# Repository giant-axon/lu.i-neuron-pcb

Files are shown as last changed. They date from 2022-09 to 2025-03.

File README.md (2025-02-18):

# Lu.i[¹](#footnote-1) – An educational neuron PCB

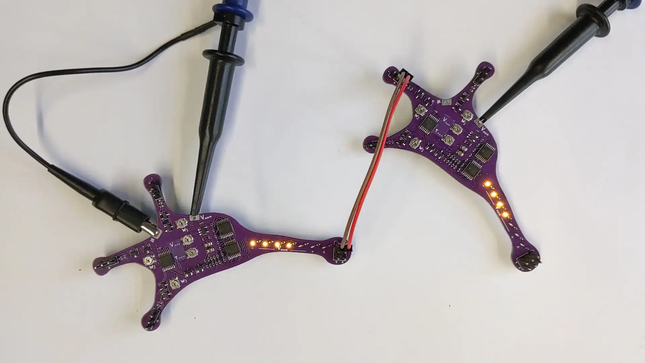
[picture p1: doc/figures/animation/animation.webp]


Lu.i is an electronic neuron circuit mimicking and illustrating the basic dynamics of real, biological neurons.
The printed circuit board (PCB) features a configurable, fully analog implementation of the leaky integrate-and-fire model and visualizes the internal state, the *membrane potential*, through a VU-meter-style chain of LEDs.
The neuron emits a short pulse whenever the membrane potential crosses a predefined threshold voltage.
Neurons communicate by exchanging these *spikes*.
Multiple boards can be connected via jumper wires to form networks.

<br/>

For a more detailed write-up you may refer to our manuscript:

**Lu. i – A low-cost electronic neuron for education and outreach**  
Yannik Stradmann, Julian Göltz, Mihai A. Petrovici, Johannes Schemmel, Sebastian Billaudelle (2025)  
Trends in Neuroscience and Education, Volume 38, 100248: [10.1016/j.tine.2025.100248](https://doi.org/10.1016/j.tine.2025.100248)

For inquiries feel free to contact us at [info@giantaxon.org](mailto:info@giantaxon.org).

## Features
- fully analog implementation of the leaky integrate-and-fire model
- configurable leak potential and membrane time constant
- three synapses with tunable weight and sign (excitatory or inhibitory) and shared synaptic time constant
- three output terminals to forward spikes to other neurons
- powered by a CR2032 coin battery
- Arduino-compatible (5V-tolerant spike IO)
- VU-meter-style visualization of the membrane potential and spike LED
- optimized for low-cost production (~ 3 € per neuron)

## Example Networks
Resembling the structure of the nervous system, multiple *Lu.i* boards can be connected to form complex neural networks.
They may be used for illustrative purposes, mimicking biological behavior, or even solving functional tasks.
The following hierarchical network, e.g., implements an *exclusive OR* (XOR).

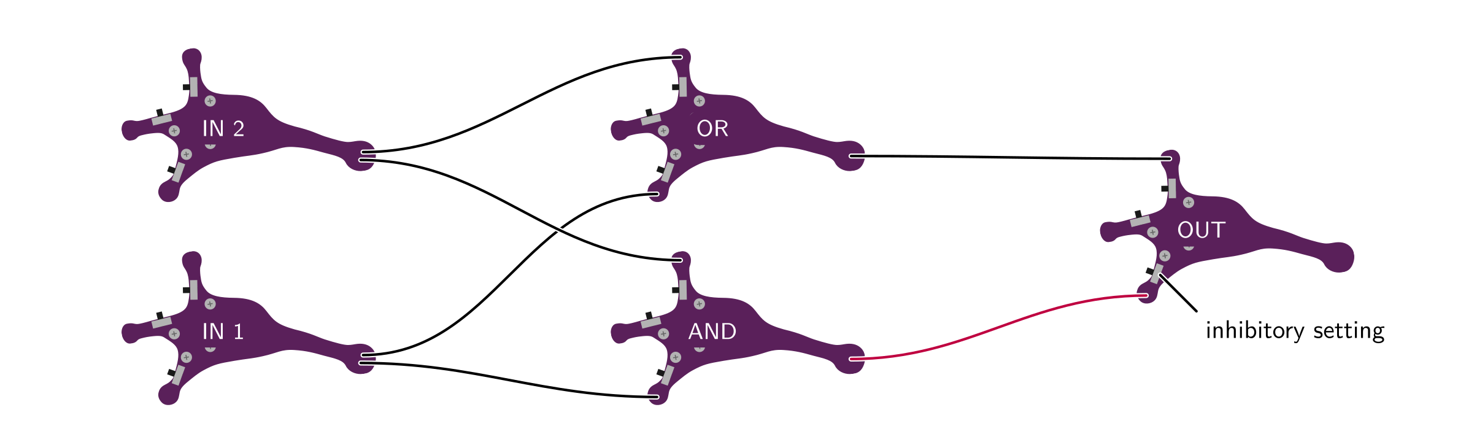
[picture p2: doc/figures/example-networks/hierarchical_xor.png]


For a more extensive list of example networks please refer to [Lu.i's documentation](doc/).

## Model
The neuron implemented on the PCBs is called Leaky Integrate-and-Fire (LIF) model.
For this model, the membrane voltage follows the dynamics described by the differential equation

$$
    \tau_\text{mem} \frac{\mathrm{d}V_\text{mem}}{\mathrm{d}t} = - \left(V_\text{mem} - V_\text{leak} \right) + I_{\text{syn}} / g_\text{leak}.
$$

In short, the neuron sums up its input $I_\text{syn}$ and decays back to the leak voltage $V_\text{leak}$.
The LIF model, including the spiking behavior when the threshold is reached, is implemented in electric circuits.

## Electronic Implementation
The following circuit diagram shows the different functional blocks of the analog implementation on *Lu.i*.
The full schematics are given as KiCAD design files.

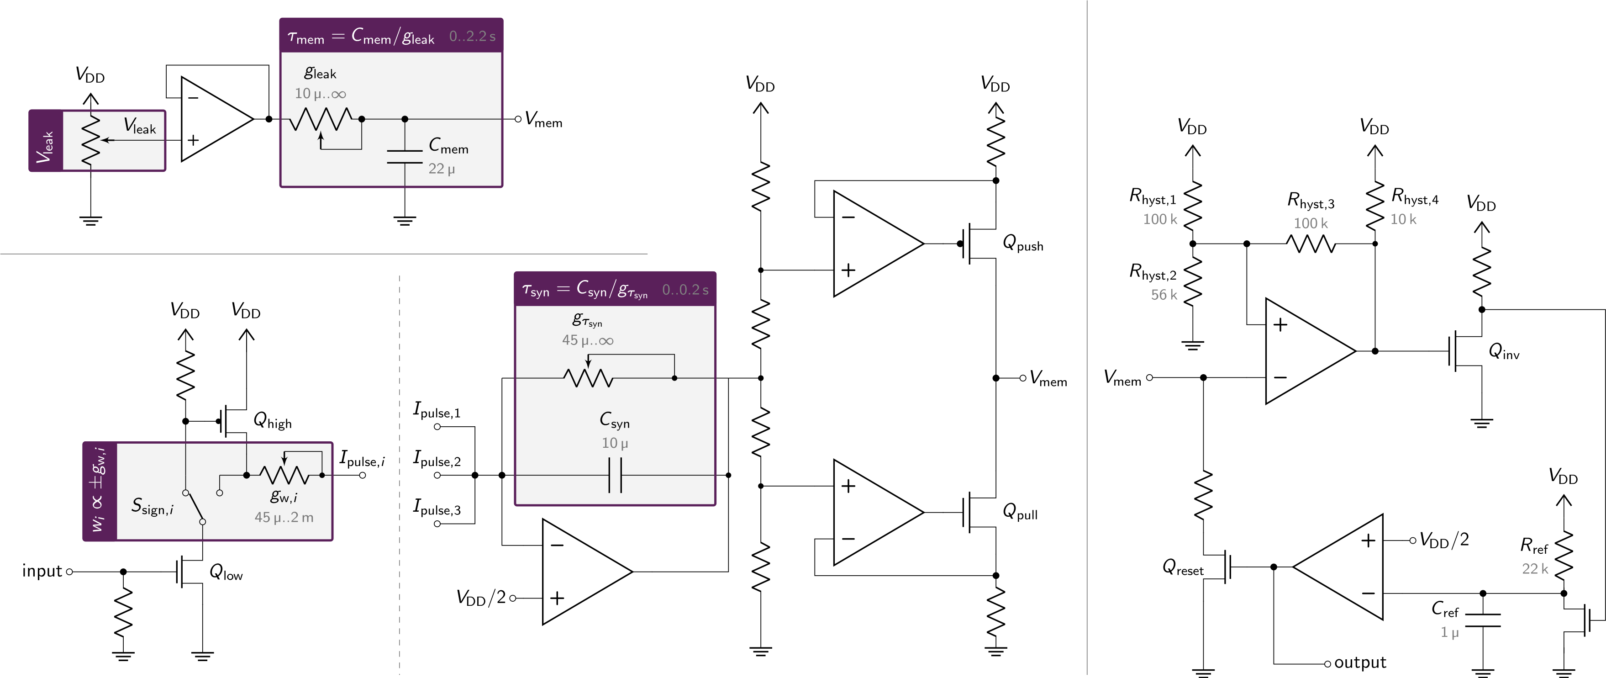
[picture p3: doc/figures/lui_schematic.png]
schematics


Besides the formation of synaptic connections between the individual neurons, inputs and outputs of each *Lu.i* can also be used to connect with a wide range of microcontrollers and sensors.
Example code can be found in the [documentation](doc/). 

## Manufacturing
The component choice in the *Lu.i* design is optimized for manufacturing at [JLCPCB](https://jlcpcb.com/).
With every [release](../../releases/), we include all the design files necessary for production.
Detailed instructions on the ordering process can be found in the [documentation](doc/).

---

<a name="footnote-1">¹</a> The name »Lu.i« (phonetic notation of »Louis«) is a tribute to Louis E. Lapicque, who first formulated the leaky integrate-and-fire equations modeling the dynamics of a neuron.

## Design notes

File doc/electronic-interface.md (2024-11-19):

# Lu.i's electronic interface

Each *Lu.i* neuron receives synaptic stimuli and sends out spike events in the form of rectangular pulses.

## Output signals
Each efferent spike creates a low-impedance voltage pulse at the axonal terminal of *Lu.i*.
These pulses are approximately 15 ms long and have a signal level of 2.5 V:

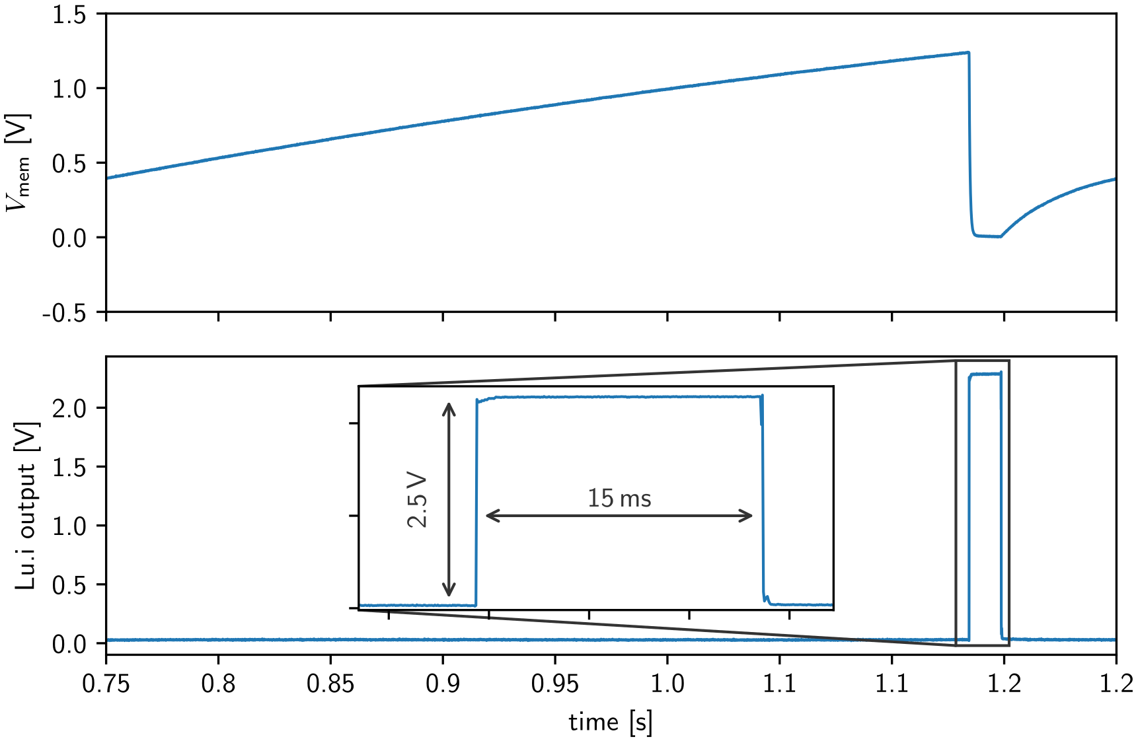
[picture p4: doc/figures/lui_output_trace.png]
Lui output trace


## Input signals
*Lu.i* decodes any voltage pulses above 1.8 V as an input event.
The amplitude does not scale the strength of the corresponding current and may therefore be of any value between 1.8 V and 20 V.
The pulse width, however, linearly scales the effective weight.

Users may create such input stimuli by external microcontrollers or sensors.
To ensure similar effective weights for such "virtual" inputs compared to other *Lu.i* neurons, the pulse length should be approximately 15 ms long.

## Example: Stimulus generation with Arduino
Using the common [Arduino](https://www.arduino.cc/) framework, we can define a simple function to create input stimuli.
For example, we can create a regular-spaced spike train:
```cpp
// Arduino pin connected to the Lu.i synapse
static constexpr uint8_t NEURON_PIN = 5;

void send_spike(uint8_t neuron_pin)
{
	digitalWrite(neuron_pin, true);
	delay(15);  // 15ms pulse length
	digitalWrite(neuron_pin, false);
}

void setup()
{
	pinMode(NEURON_PIN, OUTPUT);
}

void loop()
{
	send_spike(NEURON_PIN);
	delay(500); // 500ms inter spike interval
}
```

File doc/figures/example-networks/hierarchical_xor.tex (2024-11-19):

\documentclass[convert={density=300,outext=.png}]{standalone}
\input{preamble.tex}

\begin{document}

\tikzset{
  symbolGround/.pic = {
      \node(-m) [pic actions]{};
      \begin{scope}
          \draw[line cap=round] (0, 0) -- (0, 0.2);
          \draw[line cap=round] (-0.3, 0) -- (0.3, 0);
          \draw[line cap=round] (-0.2, -0.1) -- (0.2, -0.1);
          \draw[line cap=round] (-0.1, -0.2) -- (0.1, -0.2);
      \end{scope}
  },
  symbolMinus/.pic = {
      \node(-m) [pic actions]{};
      \begin{scope}
          \draw[line cap=round] (-0.2, 0) -- (0.2, 0);
      \end{scope}
  },
  symbolPlus/.pic = {
      \node(-m) [pic actions]{};
      \begin{scope}
          \draw[line cap=round] (0, -0.2) -- (0, 0.2);
          \draw[line cap=round] (-0.2, 0) -- (0.2, 0);
      \end{scope}
  }
}

\begin{tikzpicture}[
    scale=1.,
    >=latex,
    transform shape,
]
    \def\numNeuronsI{2}
    \def\numNeuronsH{2}
    \def\numNeuronsO{1}
    \def\scale{1.7}

    \def\posXI{-7}
    \def\posXH{-0.25}
    \def\posXO{6.5}

    \def\lengthSeparation{2.8}

    \def\angleNeuron{10}
    \def\angleOut{0}
    \def\angleIn{180}

    \foreach \i in {1,...,\numNeuronsI}
    {
        \pgfmathsetmacro\posYtmp{0 + \lengthSeparation * (\i - (\numNeuronsI + 1) / 2)}
        \pcbNeuron{neuron-I\i}{
            \posXI, \posYtmp
        }{\scale}{\angleNeuron}{}{}{tunab};
    }

    \foreach \i in {1,...,\numNeuronsH}
    {
        \pgfmathsetmacro\posYtmp{0 + \lengthSeparation * (\i - (\numNeuronsH + 1) / 2)}
        \pcbNeuron{neuron-H\i}{
            \posXH, \posYtmp
        }{\scale}{\angleNeuron}{}{}{tunab};
    }

    \foreach \i in {1,...,\numNeuronsO}
    {
        \pgfmathsetmacro\posYtmp{0 + \lengthSeparation * (\i - (\numNeuronsO + 1) / 2)}
        \pcbNeuron{neuron-O\i}{
            \posXO, \posYtmp
        }{\scale}{\angleNeuron}{}{}{tunab};
    }

    % %%%%%%%%%%%%% connections
    % % input hidden
    \draw[connection] (neuron-I1-Ac) to[out=\angleOut,in=\angleIn] (neuron-H1-Dc);
    \draw[connection] (neuron-I1-Aa) to[out=\angleOut,in=\angleIn] (neuron-H2-Dc);
    %
    \draw[connection] (neuron-I2-Ac) to[out=\angleOut,in=\angleIn] (neuron-H1-Da);
    \draw[connection] (neuron-I2-Aa) to[out=\angleOut,in=\angleIn] (neuron-H2-Da);

    % % hidden output
    \draw[connection, purple] (neuron-H1-Ab) to[out=\angleOut,in=\angleIn] (neuron-O1-Dc);
    %
    \draw[connection] (neuron-H2-Ab) to[out=\angleOut,in=\angleIn] (neuron-O1-Da);
    %

    % %%%%%%%%%%%%% labels
    \tikzstyle{specialNeuronlabel} = [neuronlabel, fill=pcbcolour, rounded corners=.15cm]
    \node[specialNeuronlabel] at (neuron-I1-l) {IN 1};
    \node[specialNeuronlabel] at (neuron-I2-l) {IN 2};
    \node[specialNeuronlabel] at (neuron-H1-l) {AND};
    \node[specialNeuronlabel] at (neuron-H2-l) {OR};
    \node[specialNeuronlabel] at (neuron-O1-l) {OUT};

    % redraw inhibitory switch
    \node[anchor=north west] (tmp) at ([xshift=0.5cm, yshift=-0.5cm]neuron-O1-tun-WSc) {inhibitory setting};
    \draw[connection] (neuron-O1-tun-WSc) -- (tmp.north west);
	
    \begin{scope}[on background layer]
    	\node[minimum width=20cm, fit=(current bounding box.north west) (current bounding box.south east), inner sep=2pt, fill=white] {};
    \end{scope}
\end{tikzpicture}
\end{document}

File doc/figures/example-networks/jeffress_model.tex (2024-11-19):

\documentclass[convert={density=300,outext=.png}]{standalone}
\nonstopmode
\input{preamble.tex}

\begin{document}

\begin{tikzpicture}[
    scale=1.,
    >=latex,
    transform shape,
]
    \def\numNeurons{4}
    \def\scale{1.3}
    \def\halfAngleConnection{10}
    \def\angleNeuron{10}
    \def\posXoffsetTop{-10.4}
    \def\posXoffsetMiddle{-8.0}
    \def\posXoffsetBottom{-3.4}
    \def\lengthSeparation{3.5}
    \def\angleOut{-20}
    \def\angleIn{180}

    % % draw ellipse on which the neurons lie
    % \draw (0,0) ellipse (\axlengthA cm and \axlengthB cm );

    % neurons
    \foreach \i in {2,...,\numNeurons}
    {
        % delay Top
        \pcbNeuron{nDelayTop-\i}{
            \posXoffsetTop + \i * \lengthSeparation, 3
        }{\scale}{\angleNeuron}{}{}{};
        % delay bottm
        \pgfmathsetmacro{\xPosition}{\posXoffsetBottom + (\numNeurons - \i) * \lengthSeparation}
        \pcbNeuron{nDelayBottom-\i}{
            \xPosition, -3
        }{\scale}{\angleNeuron + 180}{}{}{};

        % \node[neuronlabel, font=\sffamily\tiny, ] at (nDelayTop-\i) {nDelayTop-\i};
        % \node[neuronlabel, font=\sffamily\tiny, ] at (nDelayBottom-\i) {nDelayBottom-\i};
    }

    % coincidence
    \foreach \i in {1,...,\numNeurons}
    {
        \pcbNeuron{nCoinci-\i}{
            \posXoffsetMiddle + \i * \lengthSeparation, 0
        }{\scale}{\angleNeuron}{}{}{};

        % \node[neuronlabel, font=\sffamily\tiny, ] at (nCoinci-\i) {nCoinci-\i};
    }

    % connections Delay
    \foreach \i in {2,...,\numNeurons}
    {
        \pgfmathtruncatemacro\nexts{ifthenelse(\i==\numNeurons, 1, round(\i+1))}
        \ifthenelse{\equal{\i}{\numNeurons}}{}{
            \draw[connection] (nDelayTop-\i-Ab) to[out=\angleOut,in=\angleIn] (nDelayTop-\nexts-Db);
            \draw[connection] (nDelayBottom-\i-Ab) to[out=\angleOut+180,in=\angleIn+180] (nDelayBottom-\nexts-Db);
        }
    }

    % connections Top to coincidence
    \foreach \i in {1,...,\numNeurons}
    {
        \ifthenelse{\equal{\i}{1}}{}{
            \draw[connection] (nDelayTop-\i-Ac) to[out=\angleOut,in=\angleIn-70] (nCoinci-\i-Da);
        }
        \ifthenelse{\equal{\i}{\numNeurons}}{}{
            \pgfmathtruncatemacro\nMinusI{round(\numNeurons-\i+1)}
            \draw[connection] (nDelayBottom-\nMinusI-Ac) to[out=\angleOut+180,in=\angleIn+40] (nCoinci-\i-Dc);
        }
    }

    % external stimulus

    \coordinate (ears) at (0, -6);
    \coordinate (cableIntermediateBottom) at ([yshift=0cm, xshift=2cm]nDelayBottom-2-Db);
    \coordinate (cableIntermediateTop) at ([yshift=-2cm, xshift=-2cm]nDelayTop-2-Db);

    \draw[connection] ([xshift=1mm]ears) to[out=90, in=-90] (cableIntermediateBottom) to[out=90,in=\angleIn+180] (nDelayBottom-2-Db);
    \draw[connection] (cableIntermediateBottom) to[out=90,in=\angleIn+40] (nCoinci-4-Dc);

    \draw[connection] ([xshift=-1mm]ears) to[out=90, in=-45] ([yshift=-0.5cm, xshift=-2cm]nDelayBottom-\numNeurons) to[out=-45+180, in=-90] (cableIntermediateTop) to[out=90,in=\angleIn] (nDelayTop-2-Db);
    \draw[connection] (cableIntermediateTop) to[out=90,in=\angleIn-70] (nCoinci-1-Da);

    \begin{scope}[on background layer]
    	\node[minimum width=20cm, fit=(current bounding box.north west) (current bounding box.south east), inner sep=2pt, fill=white] {};
    \end{scope}

    \begin{scope}[on background layer]
    	\node[minimum width=20cm, fit=(current bounding box.north west) (current bounding box.south east), inner sep=2pt, fill=white] {};
    \end{scope}
\end{tikzpicture}
\end{document}

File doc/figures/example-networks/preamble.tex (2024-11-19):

\usepackage{tikz}
\usepackage{svg}

\usetikzlibrary{shapes.geometric}
\usetikzlibrary{arrows.meta}
\usetikzlibrary{positioning}
\usetikzlibrary{calc}
\usetikzlibrary{backgrounds}
\usetikzlibrary{fit}
\usetikzlibrary{fadings}
\usetikzlibrary{decorations}
\usepgflibrary{decorations.pathmorphing}
\usepgflibrary{decorations.markings}

\renewcommand{\familydefault}{\sfdefault}
\usepackage{sansmathfonts}

\usepackage{rotating}

\definecolor{pcbcolour}{RGB}{90, 32, 90}
\definecolor{VULEDon}{RGB}{255, 128, 0}
\definecolor{VULEDoff}{RGB}{229, 207, 184}
% \colorlet{VULEDoff}{VULEDon!0.9!white}%

% for organising the multi-panel figures
% \tikzset{panel/.style={inner sep=0pt, }};
% \tikzset{panellabel/.style={anchor=north west, inner sep=0pt, font={\bfseries\sffamily}}};
\tikzstyle{panel} = [
    inner sep=0pt,
]
\tikzstyle{panellabel} = [
    anchor=north west,
    inner sep=0pt,
    font={\bfseries\sffamily},
]
\definecolor{cExcitatory}{RGB}{255, 77, 77}
\definecolor{cInhibitory}{RGB}{0, 51, 204}
\definecolor{cBGInhibitory}{RGB}{153, 194, 255}

\tikzstyle{connection} = [
    line width=1.0pt,
    preaction={draw,white,line width=2pt, line cap=round},
    line cap=round,
    ]
\tikzstyle{connectionSmall} = [
    line width=0.5pt,
    preaction={draw,white,line width=1pt, line cap=round},
    line cap=round,
    ]

\tikzstyle{inhibitory} = [
    line width=1.0pt,
    color=cInhibitory,
    preaction={draw,white,line width=2pt, line cap=round, -{Bar[scale=0.4,sep=-1.0pt]}},
    -{Bar[scale=0.4,sep=-0.5pt]},
    ]
\tikzstyle{excitatory} = [
    line width=1.0pt,
    color=cExcitatory,
    preaction={draw,white,line width=2pt, line cap=round, -{Latex[round, scale=0.6,sep=-1.8pt]}},
    -{Latex[round, scale=0.6,sep=-0.4pt]},
    ]

\tikzstyle{neuronlabel} = [
    white,
    font=\sffamily\small,
    ]

\newcommand{\ledVU}[7]{
    % macro for sketch used in overviews
    % arg1: name of nodes
    % arg2: position of node 
    % arg3: argScale
    % arg4: how many membrane lights are on
    % arg5: is spikeLED on
    % arg6: fill bkgnd
    % arg7: draw
    % %%%%%%%%%%%%% draw stuff
    \ifthenelse{ \equal{#3}{} }{
        \def\argScale{1}
    }{
        \def\argScale{#3}
    }
    \pgfmathsetmacro\halfWidth{0.4mm * \argScale}
    \pgfmathsetmacro\segmentHalfHeight{0.4mm * \argScale}
    \pgfmathsetmacro\segmentSeparation{0.3mm * \argScale}
    \def\spikeSeparation{2.5}  % in fractions of segment separation
    \def\LEDseparation{0.2mm * \argScale}

    \pgfmathsetmacro\totalHeight{\segmentHalfHeight*2*7 + \segmentSeparation * (5 + \spikeSeparation) + 2 * \LEDseparation}
    \coordinate (#1) at (#2);
    \coordinate (#1-bottom) at ([yshift=-\totalHeight]#1);
    \coordinate (#1-bottomL) at ([xshift=-\halfWidth - \LEDseparation]#1-bottom);
    \coordinate (#1-bottomR) at ([xshift=\halfWidth + \LEDseparation]#1-bottom);
    \coordinate (#1-L) at ([xshift=-\halfWidth - \LEDseparation]#1);
    \coordinate (#1-R) at ([xshift=\halfWidth + \LEDseparation]#1);
    
    \def\VULEDon{VULEDon}
    \def\VULEDoff{VULEDoff}

    \ifthenelse{ \equal{#6}{} }{ \def\optBknd{none} }{ \def\optBknd{pcbcolour} }
    \ifthenelse{ \equal{#7}{} }{ \def\optDraw{none} }{ \def\optDraw{pcbcolour} }
    \draw [
        shape=rectangle, anchor=center,
        fill=\optBknd,
        draw=\optDraw,
        line width=0.4pt * \argScale,
        % decorate, decoration={
        %     zigzag,segment length=0.5mm * \argScale, amplitude=.04mm * \argScale
        % },
        % minimum width=2mm * \argScale, minimum height=8mm * \argScale,
    ] (#1-L) rectangle (#1-bottomR);

    % define coords
    \foreach \i in {0,...,5}
    {
        \pgfmathsetmacro\height{\segmentHalfHeight*(2*\i+1)+ \segmentSeparation*\i + \LEDseparation};
        \coordinate (#1-LED\i) at ([yshift=\height]#1-bottom);
    };
    \pgfmathsetmacro\height{\segmentHalfHeight*(2*6+1) + \segmentSeparation * (5 + \spikeSeparation) + \LEDseparation};
    \coordinate (#1-LEDspike) at ([yshift=\height]#1-bottom);

    % draw stuff
    \foreach \i in {0,...,5}
    {
        \pgfmathsetmacro\iPlusOne{\i + 1};
        \ifthenelse{\i < #4}{\def\state{VULEDon}}{\def\state{VULEDoff}}
        \draw [
            fill=\state,
            draw=none,
        ] ([xshift=-\halfWidth, yshift=-\segmentHalfHeight]#1-LED\i) rectangle ([xshift=\halfWidth, yshift=\segmentHalfHeight]#1-LED\i) ;
        \ifthenelse{\i < #4}{
            \foreach \a in {0, 45, 90, 135, ..., 360}
            {
            \draw[
                rotate=\a,
                shorten <=1pt,
                draw=VULEDon,
            ] (#1-LED\i) -- ++(0.08*\argScale, 0);
            }
        }{}
    };
    \ifthenelse{ \equal{#5}{} }{\def\state{VULEDoff}}{\def\state{VULEDon}}
    \draw [
        fill=\state,
        draw=none,
    ] ([xshift=-\halfWidth, yshift=-\segmentHalfHeight]#1-LEDspike) rectangle ([xshift=\halfWidth, yshift=\segmentHalfHeight]#1-LEDspike) ;
    \ifthenelse{ \equal{#5}{} }{}{
            \foreach \a in {0, 45, 90, 135, ..., 360}
            {
            \draw[
                rotate=\a,
                shorten <=1pt,
                draw=VULEDon,
            ] (#1-LEDspike) -- ++(0.08*\argScale, 0);
            }
    }
}

\newcommand{\pcbNeuron}[7]{
    % macro for sketch used in overviews
    % arg1: name of nodes
    % arg2: point of node 
    % arg3: argScale
    % arg4: rotation
    % arg5: if nonempty, use only border shape of PCB
    % arg6: if nonempty, draw LEDs (arg6 are on, if >6 spiking)
    % arg7: if nonempty, draw tunabels
    % %%%%%%%%%%%%% draw stuff

    \ifthenelse{ \equal{#3}{} }{
        \def\argScale{1}
    }{
        \def\argScale{#3}
    }
    \ifthenelse{ \equal{#4}{} }{
        \def\rot{0}
    }{
        \def\rot{#4}
    }

    \coordinate (#1) at (#2);

    % label coord
    \coordinate (#1-l) at ([yshift=0.4mm * \argScale, xshift=0.6mm * \argScale] #2);

    \node[anchor=center,
          xshift=0.25cm * \argScale,yshift=0.1cm * \argScale, 
          rotate around={\rot:(#1)},
          ] (whitehead) at (#1)
    {
        % \scaledWidth
        \scalebox{\argScale}{
            \ifthenelse{ \equal{#5}{} }{
                \includesvg[width=2cm]{neuron_filled.svg}
            }{
                \includesvg[width=2cm]{neuron_border.svg}
            }
        }
    };

    % %%%%%%%%%%%%%%%%%%% dendrites
    \pgfmathsetmacro{\lengthDaX}{-0.09cm * \argScale}
    \pgfmathsetmacro{\lengthDaY}{0.64cm * \argScale}
    \coordinate[rotate around={\rot:(#1)}] (#1-Da) at ([xshift=\lengthDaX, yshift=\lengthDaY] #1);

    \pgfmathsetmacro{\lengthDbX}{-0.685cm * \argScale}
    \pgfmathsetmacro{\lengthDbY}{0.138cm * \argScale}
    \coordinate[rotate around={\rot:(#1)}]  (#1-Db) at ([xshift=\lengthDbX, yshift=\lengthDbY] #1);

    \pgfmathsetmacro{\lengthDcX}{-0.47cm * \argScale}
    \pgfmathsetmacro{\lengthDcY}{-0.42cm * \argScale}
    \coordinate[rotate around={\rot:(#1)}]  (#1-Dc) at ([xshift=\lengthDcX, yshift=\lengthDcY] #1);

    % %%%%%%%%%%%%%%%%%%% axons
    \pgfmathsetmacro{\lengthAaX}{1.150cm * \argScale}
    \pgfmathsetmacro{\lengthAaY}{-0.360cm * \argScale}
    \coordinate[rotate around={\rot:(#1)}]  (#1-Aa) at ([xshift=\lengthAaX, yshift=\lengthAaY] #1);

    \pgfmathsetmacro{\lengthAbX}{1.135cm * \argScale}
    \pgfmathsetmacro{\lengthAbY}{-0.390cm * \argScale}
    \coordinate[rotate around={\rot:(#1)}]  (#1-Ab) at ([xshift=\lengthAbX, yshift=\lengthAbY] #1);

    \pgfmathsetmacro{\lengthAcX}{1.120cm * \argScale}
    \pgfmathsetmacro{\lengthAcY}{-0.420cm * \argScale}
    \coordinate[rotate around={\rot:(#1)}]  (#1-Ac) at ([xshift=\lengthAcX, yshift=\lengthAcY] #1);

    % %%%%%%%%%%%%%%%%%%% LEDs
    \pgfmathsetmacro{\lengthLEDX}{0.770cm * \argScale}
    \pgfmathsetmacro{\lengthLEDY}{-0.205cm * \argScale}
    \pgfmathsetmacro{\newscaling}{\argScale * 0.8}  % isn't tex beautiful..
    \coordinate[rotate around={\rot:(#1)}] (#1-LEDs) at ([xshift=\lengthLEDX, yshift=\lengthLEDY] #1);
    \ifthenelse{ \equal{#6}{} }{}{
        \ifthenelse{ #6 > 6}{
            \node[rotate=244+\rot] (tmp) at (#1-LEDs) {
                \begin{tikzpicture}[
                ]
                \ledVU{luiLED}{0, 0}{\newscaling}{0}{yes}{}{} ;
                \end{tikzpicture}
            };
        }{
            \node[rotate=244+\rot] (tmp) at (#1-LEDs) {
                \begin{tikzpicture}[
                ]
                \ledVU{luiLED}{0, 0}{\newscaling}{#6}{}{}{} ;
                \end{tikzpicture}
            };
        };
    }

    % %%%%%%%%%%%%%%%%%%% tunables
    \pgfmathsetmacro{\lengthTunPotiRad}{1.29 * \argScale}
    \pgfmathsetmacro{\lengthTunPotiScrew}{0.59 * \argScale}

    \pgfmathsetmacro{\lengthTunVleakX}{-0.059cm * \argScale}
    \pgfmathsetmacro{\lengthTunVleakY}{0.135cm * \argScale}
    \pgfmathsetmacro{\lengthTunTaumX}{-0.059cm * \argScale}
    \pgfmathsetmacro{\lengthTunTaumY}{0.029cm * \argScale}
    \pgfmathsetmacro{\lengthTunTausX}{-0.059cm * \argScale}
    \pgfmathsetmacro{\lengthTunTausY}{-0.076cm * \argScale}
    \coordinate[rotate around={\rot:(#1)}] (#1-tun-v_leak) at ([xshift=\lengthTunVleakX, yshift=\lengthTunVleakY] #1);
    \coordinate[rotate around={\rot:(#1)}] (#1-tun-taum) at ([xshift=\lengthTunTaumX, yshift=\lengthTunTaumY] #1);
    \coordinate[rotate around={\rot:(#1)}] (#1-tun-taus) at ([xshift=\lengthTunTausX, yshift=\lengthTunTausY] #1);

    % weight potis
    \pgfmathsetmacro{\lengthTunWaX}{0.0cm * \argScale}
    \pgfmathsetmacro{\lengthTunWaY}{0.264cm * \argScale}
    \pgfmathsetmacro{\lengthTunWbX}{-0.329cm * \argScale}
    \pgfmathsetmacro{\lengthTunWbY}{0.076cm * \argScale}
    \pgfmathsetmacro{\lengthTunWcX}{-0.265cm * \argScale}
    \pgfmathsetmacro{\lengthTunWcY}{-0.129cm * \argScale}
    \coordinate[rotate around={\rot:(#1)}] (#1-tun-Wa) at ([xshift=\lengthTunWaX, yshift=\lengthTunWaY] #1);
    \coordinate[rotate around={\rot:(#1)}] (#1-tun-Wb) at ([xshift=\lengthTunWbX, yshift=\lengthTunWbY] #1);
    \coordinate[rotate around={\rot:(#1)}] (#1-tun-Wc) at ([xshift=\lengthTunWcX, yshift=\lengthTunWcY] #1);

    % drawing
    \ifthenelse{ \equal{#7}{} }{}{
        \foreach \iOtherIterator in {v_leak, taum, taus, Wa, Wb, Wc}
        {
            \fill[black!30!white] (#1-tun-\iOtherIterator) circle (\lengthTunPotiRad pt) coordinate (tmp);
            \draw[black!60!white, rotate around={\rot:(tmp)}] (tmp) ++ (-\lengthTunPotiScrew pt, 0) -- ++(2 * \lengthTunPotiScrew pt, 0);
            \draw[black!60!white, rotate around={\rot:(tmp)}] (tmp) ++ (0, -\lengthTunPotiScrew pt) -- ++(0, 2 * \lengthTunPotiScrew pt);
        };
    }

    % weight switches
    \pgfmathsetmacro{\lengthTunWSaX}{-0.082cm * \argScale}
    \pgfmathsetmacro{\lengthTunWSaY}{0.394cm * \argScale}
    \pgfmathsetmacro{\lengthTunWSbX}{-0.412cm * \argScale}
    \pgfmathsetmacro{\lengthTunWSbY}{0.153cm * \argScale}
    \pgfmathsetmacro{\lengthTunWScX}{-0.329cm * \argScale}
    \pgfmathsetmacro{\lengthTunWScY}{-0.276cm * \argScale}
    \coordinate[rotate around={\rot:(#1)}] (#1-tun-WSa) at ([xshift=\lengthTunWSaX, yshift=\lengthTunWSaY] #1);
    \coordinate[rotate around={\rot:(#1)}] (#1-tun-WSb) at ([xshift=\lengthTunWSbX, yshift=\lengthTunWSbY] #1);
    \coordinate[rotate around={\rot:(#1)}] (#1-tun-WSc) at ([xshift=\lengthTunWScX, yshift=\lengthTunWScY] #1);

    % drawing
    \ifthenelse{ \equal{#7}{} }{}{
        \foreach \iOtherIterator / \angleUnrotated in {WSa/81, WSb/4, WSc/60}
        {
            \pgfmathsetmacro{\angleRotated}{\angleUnrotated + \rot}
            \fill[black!90!white, rotate around={\angleRotated:(#1-tun-\iOtherIterator)}] (#1-tun-\iOtherIterator) ++(-0.024*\argScale, 0.0) rectangle ++(0.047*\argScale, 0.118*\argScale);
            \fill[black!30!white, rotate around={\angleRotated:(#1-tun-\iOtherIterator)}] (#1-tun-\iOtherIterator) ++(-0.079*\argScale, 0.0) rectangle ++(0.159*\argScale, 0.059*\argScale);
        };
    }
}

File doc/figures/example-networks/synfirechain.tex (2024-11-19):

\documentclass[convert={density=300,outext=.png}]{standalone}
\input{preamble.tex}

\begin{document}

\begin{tikzpicture}[
    scale=1.,
    >=latex,
    transform shape,
]
    \def\numNeurons{5}
    \def\scale{1.3}
    \def\halfAngleConnection{10}
    \def\angleNeuron{10}
    \def\posXoffset{-10.4}
    \def\lengthSeparation{3.5}
    \def\angleOut{-20}
    \def\angleIn{180}

    % % draw ellipse on which the neurons lie
    % \draw (0,0) ellipse (\axlengthA cm and \axlengthB cm );

    % neurons
    \foreach \i in {1,...,\numNeurons}
    {
        \pcbNeuron{neuron-\i}{
            \posXoffset + \i * \lengthSeparation, 0
        }{\scale}{\angleNeuron}{}{}{};
    }

    % connections
    \foreach \i in {1,...,\numNeurons}
    {
        \pgfmathtruncatemacro\nexts{ifthenelse(\i==\numNeurons, 1, round(\i+1))}
        \ifthenelse{\equal{\i}{\numNeurons}}{}{
            \draw[connection] (neuron-\i-Ab) to[out=\angleOut,in=\angleIn] (neuron-\nexts-Db);
        }
    }

    \begin{scope}[on background layer]
    	\node[minimum width=20cm, fit=(current bounding box.north west) (current bounding box.south east), inner sep=2pt, fill=white] {};
    \end{scope}

    \begin{scope}[on background layer]
    	\node[minimum width=20cm, fit=(current bounding box.north west) (current bounding box.south east), inner sep=2pt, fill=white] {};
    \end{scope}
\end{tikzpicture}
\end{document}

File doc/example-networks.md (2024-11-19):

# Example networks

## Synfire chain
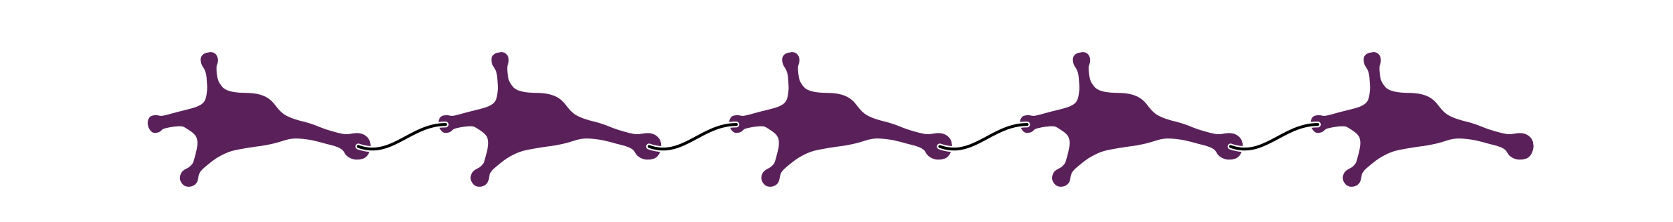
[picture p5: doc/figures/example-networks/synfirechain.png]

The name synfire chain is an abbreviation for synchronous firing chain and describes a circular feed-forward chain, in which activity travels from layer to layer.
When suitably configured, a spike in one of our neurons will elicit a consecutive spike in the next neuron in the chain.

This can also be put in a circular shape where the activity travels indefinitely.
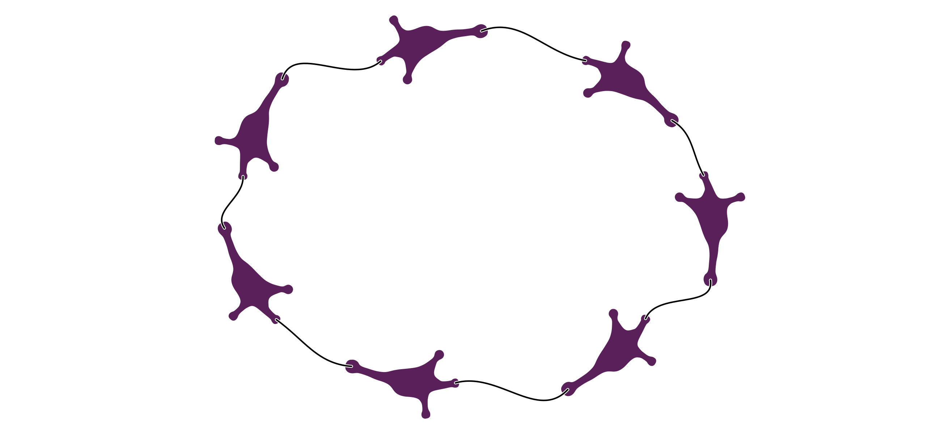
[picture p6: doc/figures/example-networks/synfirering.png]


Two synfirechains together with a set of coincidence-detecting neurons, can be used to realise a simplified version of the [Jeffress model](http://www.scholarpedia.org/article/Jeffress_model):
given two stimuli, their time difference determines which of the coincidence neurons is activated.
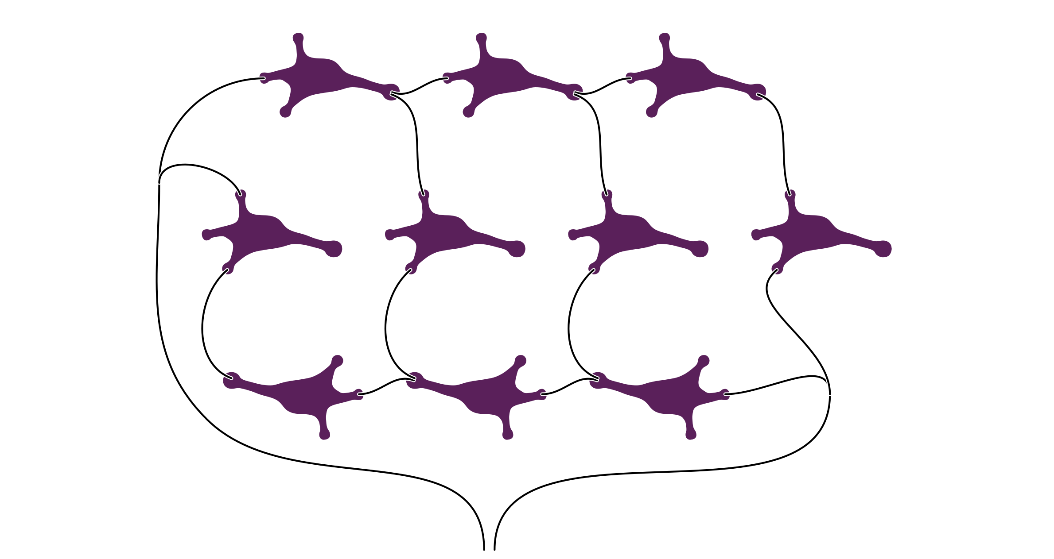
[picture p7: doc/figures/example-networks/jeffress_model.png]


## General hierarchical network
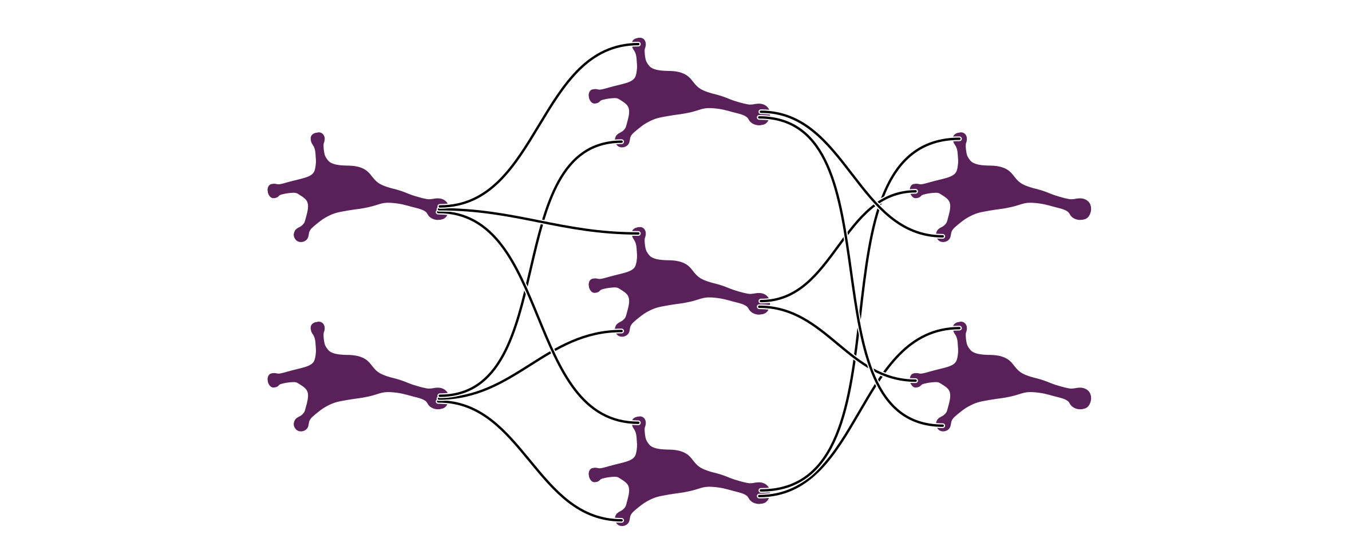
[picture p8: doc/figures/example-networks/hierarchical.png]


## Solving the XOR problem rate based


## Ring attractor
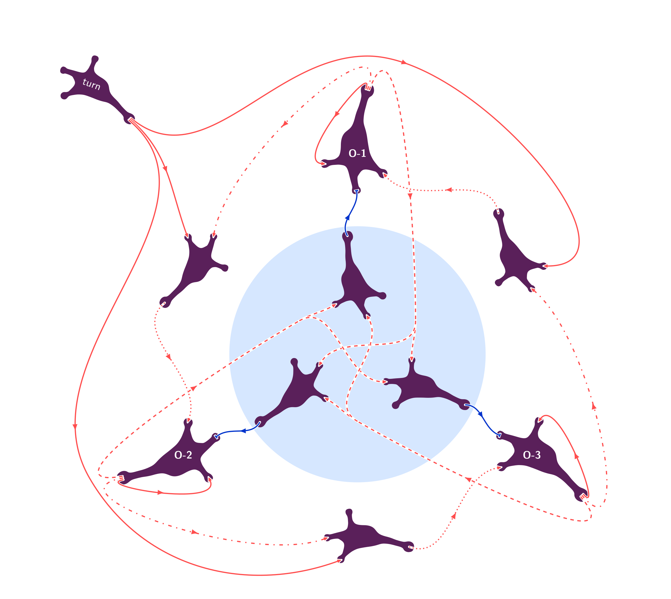
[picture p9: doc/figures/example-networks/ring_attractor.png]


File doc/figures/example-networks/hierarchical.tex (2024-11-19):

\documentclass[convert={density=300,outext=.png}]{standalone}
\input{preamble.tex}

\begin{document}
\begin{tikzpicture}[
    scale=1.,
    >=latex,
    transform shape,
]
    \def\numNeuronsI{2}
    \def\numNeuronsH{3}
    \def\numNeuronsO{2}
    \def\scale{1.3}

    \def\posXI{-5}
    \def\posXH{-0.25}
    \def\posXO{4.5}

    \def\lengthSeparation{2.8}

    \def\angleNeuron{10}
    \def\angleOut{0}
    \def\angleIn{180}

    \foreach \i in {1,...,\numNeuronsI}
    {
        \pgfmathsetmacro\posYtmp{0 + \lengthSeparation * (\i - (\numNeuronsI + 1) / 2)}
        \pcbNeuron{neuron-I\i}{
            \posXI, \posYtmp
        }{\scale}{\angleNeuron}{}{}{};
    }

    \foreach \i in {1,...,\numNeuronsH}
    {
        \pgfmathsetmacro\posYtmp{0 + \lengthSeparation * (\i - (\numNeuronsH + 1) / 2)}
        \pcbNeuron{neuron-H\i}{
            \posXH, \posYtmp
        }{\scale}{\angleNeuron}{}{}{};

    }

    \foreach \i in {1,...,\numNeuronsO}
    {
        \pgfmathsetmacro\posYtmp{0 + \lengthSeparation * (\i - (\numNeuronsO + 1) / 2)}
        \pcbNeuron{neuron-O\i}{
            \posXO, \posYtmp
        }{\scale}{\angleNeuron}{}{}{};
    }

    % %%%%%%%%%%%%% connections
    % % input hidden
    \draw[connection] (neuron-I1-Ac) to[out=\angleOut,in=\angleIn] (neuron-H1-Dc);
    \draw[connection] (neuron-I1-Ab) to[out=\angleOut,in=\angleIn] (neuron-H2-Dc);
    \draw[connection] (neuron-I1-Aa) to[out=\angleOut,in=\angleIn] (neuron-H3-Dc);
    %
    \draw[connection] (neuron-I2-Ac) to[out=\angleOut,in=\angleIn] (neuron-H1-Da);
    \draw[connection] (neuron-I2-Ab) to[out=\angleOut,in=\angleIn] (neuron-H2-Da);
    \draw[connection] (neuron-I2-Aa) to[out=\angleOut,in=\angleIn] (neuron-H3-Da);

    % % hidden output
    \draw[connection] (neuron-H1-Ac) to[out=\angleOut,in=\angleIn] (neuron-O1-Da);
    \draw[connection] (neuron-H1-Aa) to[out=\angleOut,in=\angleIn] (neuron-O2-Da);
    %
    \draw[connection] (neuron-H2-Ac) to[out=\angleOut,in=\angleIn] (neuron-O1-Db);
    \draw[connection] (neuron-H2-Aa) to[out=\angleOut,in=\angleIn] (neuron-O2-Db);
    %
    \draw[connection] (neuron-H3-Ac) to[out=\angleOut,in=\angleIn] (neuron-O1-Dc);
    \draw[connection] (neuron-H3-Aa) to[out=\angleOut,in=\angleIn] (neuron-O2-Dc);
	
    \begin{scope}[on background layer]
    	\node[minimum width=20cm, fit=(current bounding box.north west) (current bounding box.south east), inner sep=2pt, fill=white] {};
    \end{scope}
\end{tikzpicture}
\end{document}

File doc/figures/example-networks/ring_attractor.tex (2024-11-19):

\documentclass[convert={density=300,outext=.png}]{standalone}
\nonstopmode
\input{preamble.tex}

\begin{document}

\begin{tikzpicture}[
    scale=1.,
    >=latex,
    transform shape,
    decoration={
        markings,
        mark=at position 0.5 with {\arrow{>}}},
]
    \def\numNeurons{3}
    \def\scale{1.3}
    \def\nOrientationScale{1.6}
    \def\nOrientationRadius{6}
    \def\nOrientationAngle{10}
    \def\nInhibRadius{2.0}
    \def\nInhibAngle{30}
    \def\nSwitchRadius{5.5}
    \def\nSwitchAngle{160}
    \def\nTurnAngle{-20}

    \tikzstyle{signalSelfExc} = [excitatory, solid]
    \tikzstyle{signalToSwitch} = [excitatory, loosely dashdotted]
    \tikzstyle{signalSwitch} = [excitatory, dotted]
    \tikzstyle{signalToInhib} = [excitatory, dashed]
    \tikzstyle{signalTurn} = [excitatory, solid]

    \draw[draw=none, fill=cBGInhibitory!40] (0,0) circle (\nInhibRadius + \scale * 1.4);

    % neurons
    \foreach \i in {1,...,\numNeurons}
    {
        \pgfmathsetmacro\angle{360/\numNeurons * (\i-1) + 90}

        \pcbNeuron{nOrientation-\i}{
            {\angle}:\nOrientationRadius
        }{\nOrientationScale}{\angle + \nOrientationAngle}{}{}{};
        \node[neuronlabel] at (nOrientation-\i) {\textbf{O-\i}};

        \pcbNeuron{nInhib-\i}{
            {\angle}:\nInhibRadius
        }{\scale}{\angle + \nInhibAngle}{}{}{};

        \pcbNeuron{nSwitch-\i}{
            {\angle + 180 / \numNeurons}:\nSwitchRadius
        }{\scale}{\angle + \nSwitchAngle}{}{}{};

    }
    \pcbNeuron{nTurn}{-8, 8}{\scale}{\nTurnAngle}{}{}{};
    \node[neuronlabel, rotate=\nTurnAngle] at (nTurn-l) {turn};

    % connections
    \foreach \i in {1,...,\numNeurons}
    {
        \pgfmathsetmacro\angle{360/\numNeurons * (\i-1) + 90}

        \pgfmathtruncatemacro\iPlusOne{round(Mod(\i + 1 - 1, 3) + 1)}
        \pgfmathtruncatemacro\iPlusTwo{round(Mod(\i + 2 - 1, 3) + 1)}
        \pgfmathsetmacro\anglePlusOne{360/\numNeurons * (\iPlusOne-1) + 90}
        \pgfmathsetmacro\anglePlusTwo{360/\numNeurons * (\iPlusTwo-1) + 90}

        % self connections
        \draw[signalSelfExc, postaction={decorate}] (nOrientation-\i-Aa) to[out=\angle + \nOrientationAngle-30,in=\angle + \nOrientationAngle+180-105] (nOrientation-\i-Da);

        % inhibitory
        \draw[inhibitory, postaction={decorate}] (nInhib-\i-Ab) to[out=\angle + \nInhibAngle,in=\angle + \nOrientationAngle+180] (nOrientation-\i-Db);

        % to inhibitory
        \draw[signalToInhib, postaction={decorate}] (nOrientation-\i-Ac)
            to[out=\angle + \nOrientationAngle-30,
                in=\angle-0] (\angle - 180 / \numNeurons:\nInhibRadius)
            to[out=\angle-0+180,
               in=\anglePlusTwo + \nOrientationAngle+180-70] (nInhib-\iPlusTwo-Da);
        \draw[signalToInhib] (\angle - 180 / \numNeurons:\nInhibRadius)
            to[out=\angle-0+180,
               in=\anglePlusOne + \nOrientationAngle+180-70+ 90] (nInhib-\iPlusOne-Db);

           % switch
        \draw[signalSwitch, postaction={decorate}] (nSwitch-\i-Ab) to[out=\angle + \nOrientationAngle+\nSwitchAngle+180/\numNeurons - 100,in=\angle + \nOrientationAngle-30] (nOrientation-\iPlusOne-Dc);

        % to switch
        \draw[signalToSwitch, postaction={decorate}] (nOrientation-\i-Ab) to[out=\angle + \nOrientationAngle-30,in=\angle + \nOrientationAngle+\nSwitchAngle+180/\numNeurons + 120] (nSwitch-\i-Db);

    }

    % from turn
    \draw[signalTurn, postaction={decorate}] (nTurn-Aa) to[out=\nTurnAngle - 20,in=180] ([yshift=1cm]nOrientation-1-Ab) to[out=0,in=0] (nSwitch-3-Dc);
    \draw[signalTurn, postaction={decorate}] (nTurn-Ab) to[out=\nTurnAngle - 20,in=110]  (nSwitch-1-Dc);
    \def\tmp{120}
    \draw[signalTurn, postaction={decorate}] (nTurn-Ac) to[out=\nTurnAngle - 20,in=\tmp] ([xshift=-1cm]nOrientation-2-Ab) to[out=\tmp+180,in=200] (nSwitch-2-Dc);

    \begin{scope}[on background layer]
    	\node[minimum width=20cm, fit=(current bounding box.north west) (current bounding box.south east), inner sep=2pt,
            fill=white,
            ] {};
    \end{scope}
\end{tikzpicture}
\end{document}

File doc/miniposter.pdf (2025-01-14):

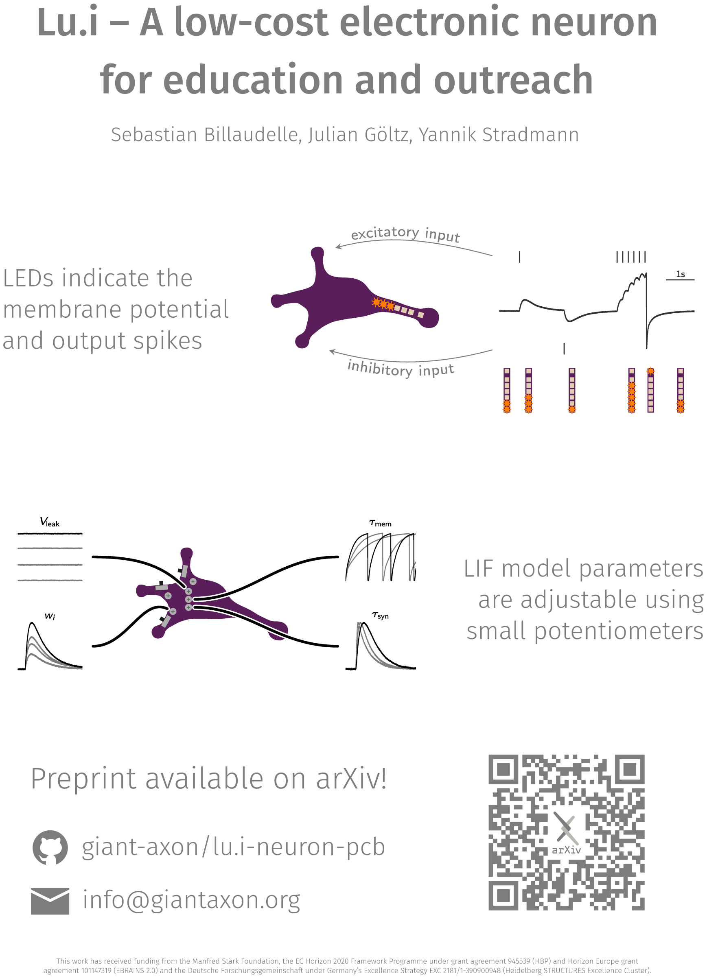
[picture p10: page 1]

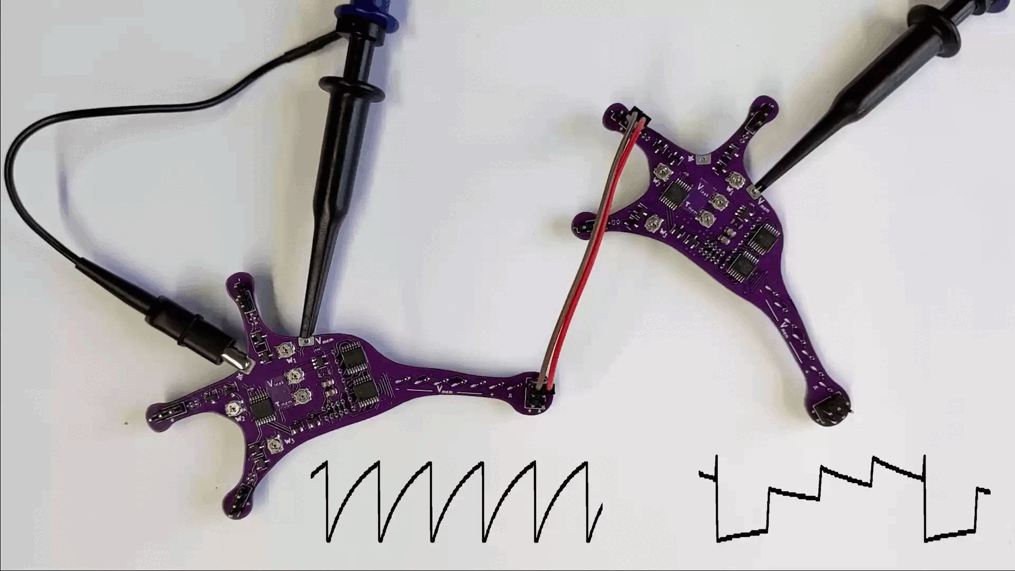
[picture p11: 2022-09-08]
doc/animation.gif

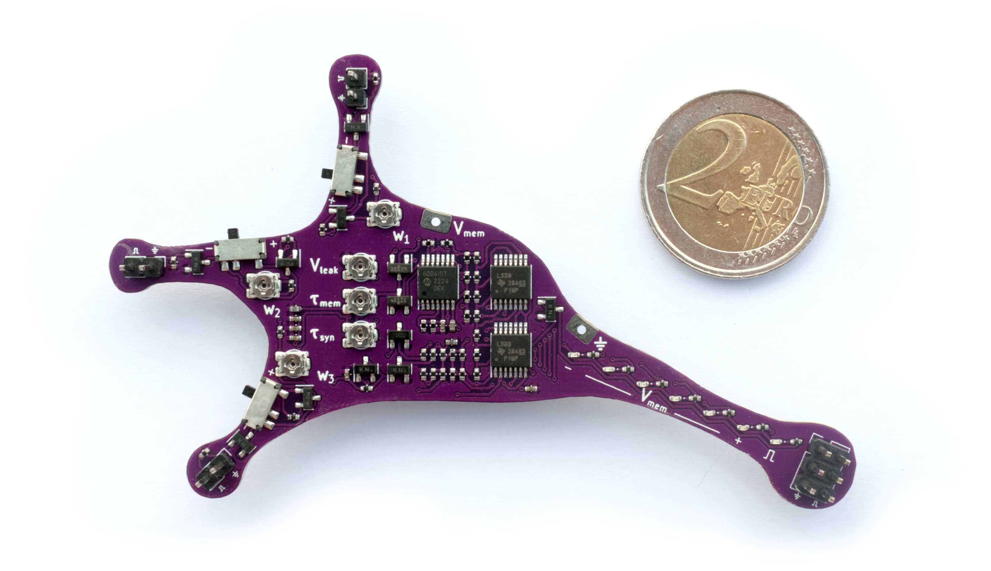
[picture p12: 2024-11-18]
doc/figures/photograph-coin.jpg

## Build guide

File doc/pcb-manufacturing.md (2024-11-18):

# Manufacturing of Lu.i boards
With every [release](../../../releases), we provide the necessary production files for orders at [JLCPCB](https://jlcpcb.com/).
We have used this manufacturer for over 1000 boards in multiple batches for the fabrication of the actual PCB as well as its assembly (PCBA).

> [!CAUTION]
> Although we never had issues during production and publish the production files to the best of our knowledge, we cannot take any liability for failed/disfunctional production runs.
Use this manual at your own risk.

## File structure
In our releases, you will find a file called `jlcpcb.zip`, which contains the following files:
```
jlcpcb.zip
├── …
├── production_files
│   ├── BOM-neuron.csv
│   ├── CPL-neuron.csv
│   └── GERBER-neuron.zip
└── …
```

* **GERBER-neuron.zip** contains the PCB production data in Gerber format, i.e., the layout of connections on the board, drilling information etc.
* **BOM-neuron.csv** contains the *bill of materials*, i.e., a list of all components on the board 
* **CPL-neuron.csv** contains the *component placement* information, i.e., where the components from the BOM should be placed during assembly

## Ordering process
Once you have created an account at JLCPCB and logged in, you can

### 1. Construct the PCB
- Upload the `GERBER-neuron.zip` and wait for processing
- The web interface wil automatically determine the number of layers (2), PCB size etc.
- Specify your *Lu.i* version at will, most importantly: PCB quantity.
  We've found that purple works great as PCB color.
  The design has no special requirements on copper weight, via structure etc. – the defaults should be good enough
- We like to remove the order number to clean up the silk screen
- We usually ask for a confirmation of the production file

### 2. Configure PCBA
- Enable the PCBA option (let JLCPCB assemble all components for you)
- Since *Lu.i* has components on both sides, a full production run requires "Standard" type and double-sided assembly.
- Just to be sure, we usually ask for a confirmation of the parts placement

> [!TIP]
> The bottom side only contains the battery holder and power switch.
Experts may select "top only" assembly, order remaining components independently and solder themselves.

### 3. Process BOM and CPL file
- In the next step, JLCPCB will ask you for the BOM and CPL files
- After processing, you may need to select alternative parts in case of shortfall (depends on your order quantity).
  For this step, a background in electronics can be handy.
  Alternatively, you may try to wait until missing components are re-stocked.
  If in doubt, ask your local expert :)
- Check the 3D model for obvious misplacement of any component

### 4. Place the order
> [!NOTE]
> *Lu.i* is published under the very permissive [CERN-OHL-S](../LICENSE) license.
If you want to fabricate your own version, please make sure to check that potential modifications comply.

- To add the design to your cart, you will need to specify a product category.
  We usually use `Education/Others` and mention the `TARIC ID 902300` ("Instruments, apparatus and models designed for demonstrational purposes, e.g. in education or exhibitions, unsuitable for other uses")
- Place and pay for the order

### 5. Post-order information
- JLCPCB will embed each *Lu.i* board in a rectangular frame to enable processing and assembly.
  When confirming the production files, make sure that the engineers don't place too many breakaway tabs (4 has worked for us in the past) – you will need to file these off manually to ensure safe handling.
  Make sure that they are not placed at the membrane voltage edge connectors.

## Post-production
- Once you receive your order, break out the individual neuron boards from their frame
- File/mill off sharp remainders of the breakaway tabs
- We are always happy to receive pictures of your orders at [info@giantaxon.org](mailto:info@giantaxon.org)! :)

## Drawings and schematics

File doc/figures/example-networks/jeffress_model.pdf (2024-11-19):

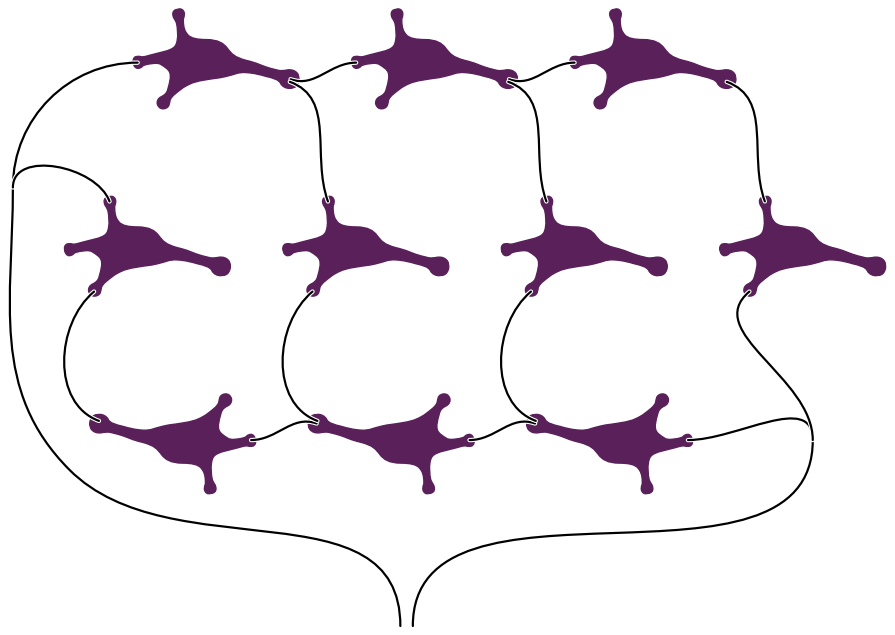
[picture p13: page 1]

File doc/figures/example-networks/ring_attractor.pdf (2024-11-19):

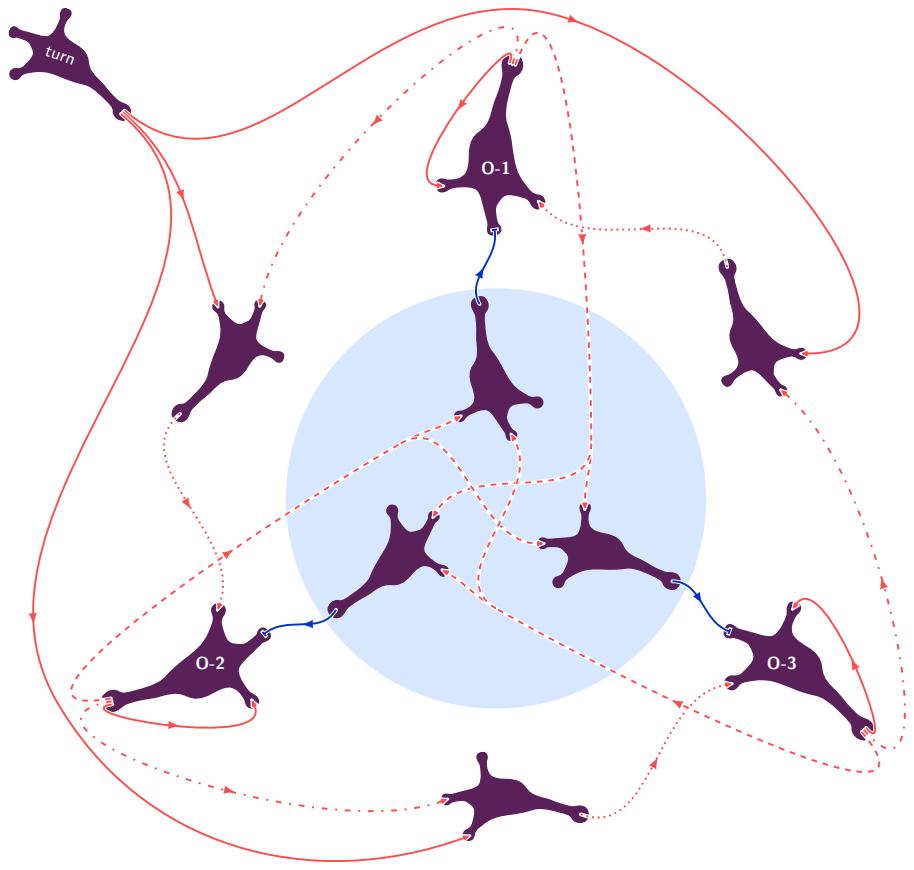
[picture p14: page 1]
turn

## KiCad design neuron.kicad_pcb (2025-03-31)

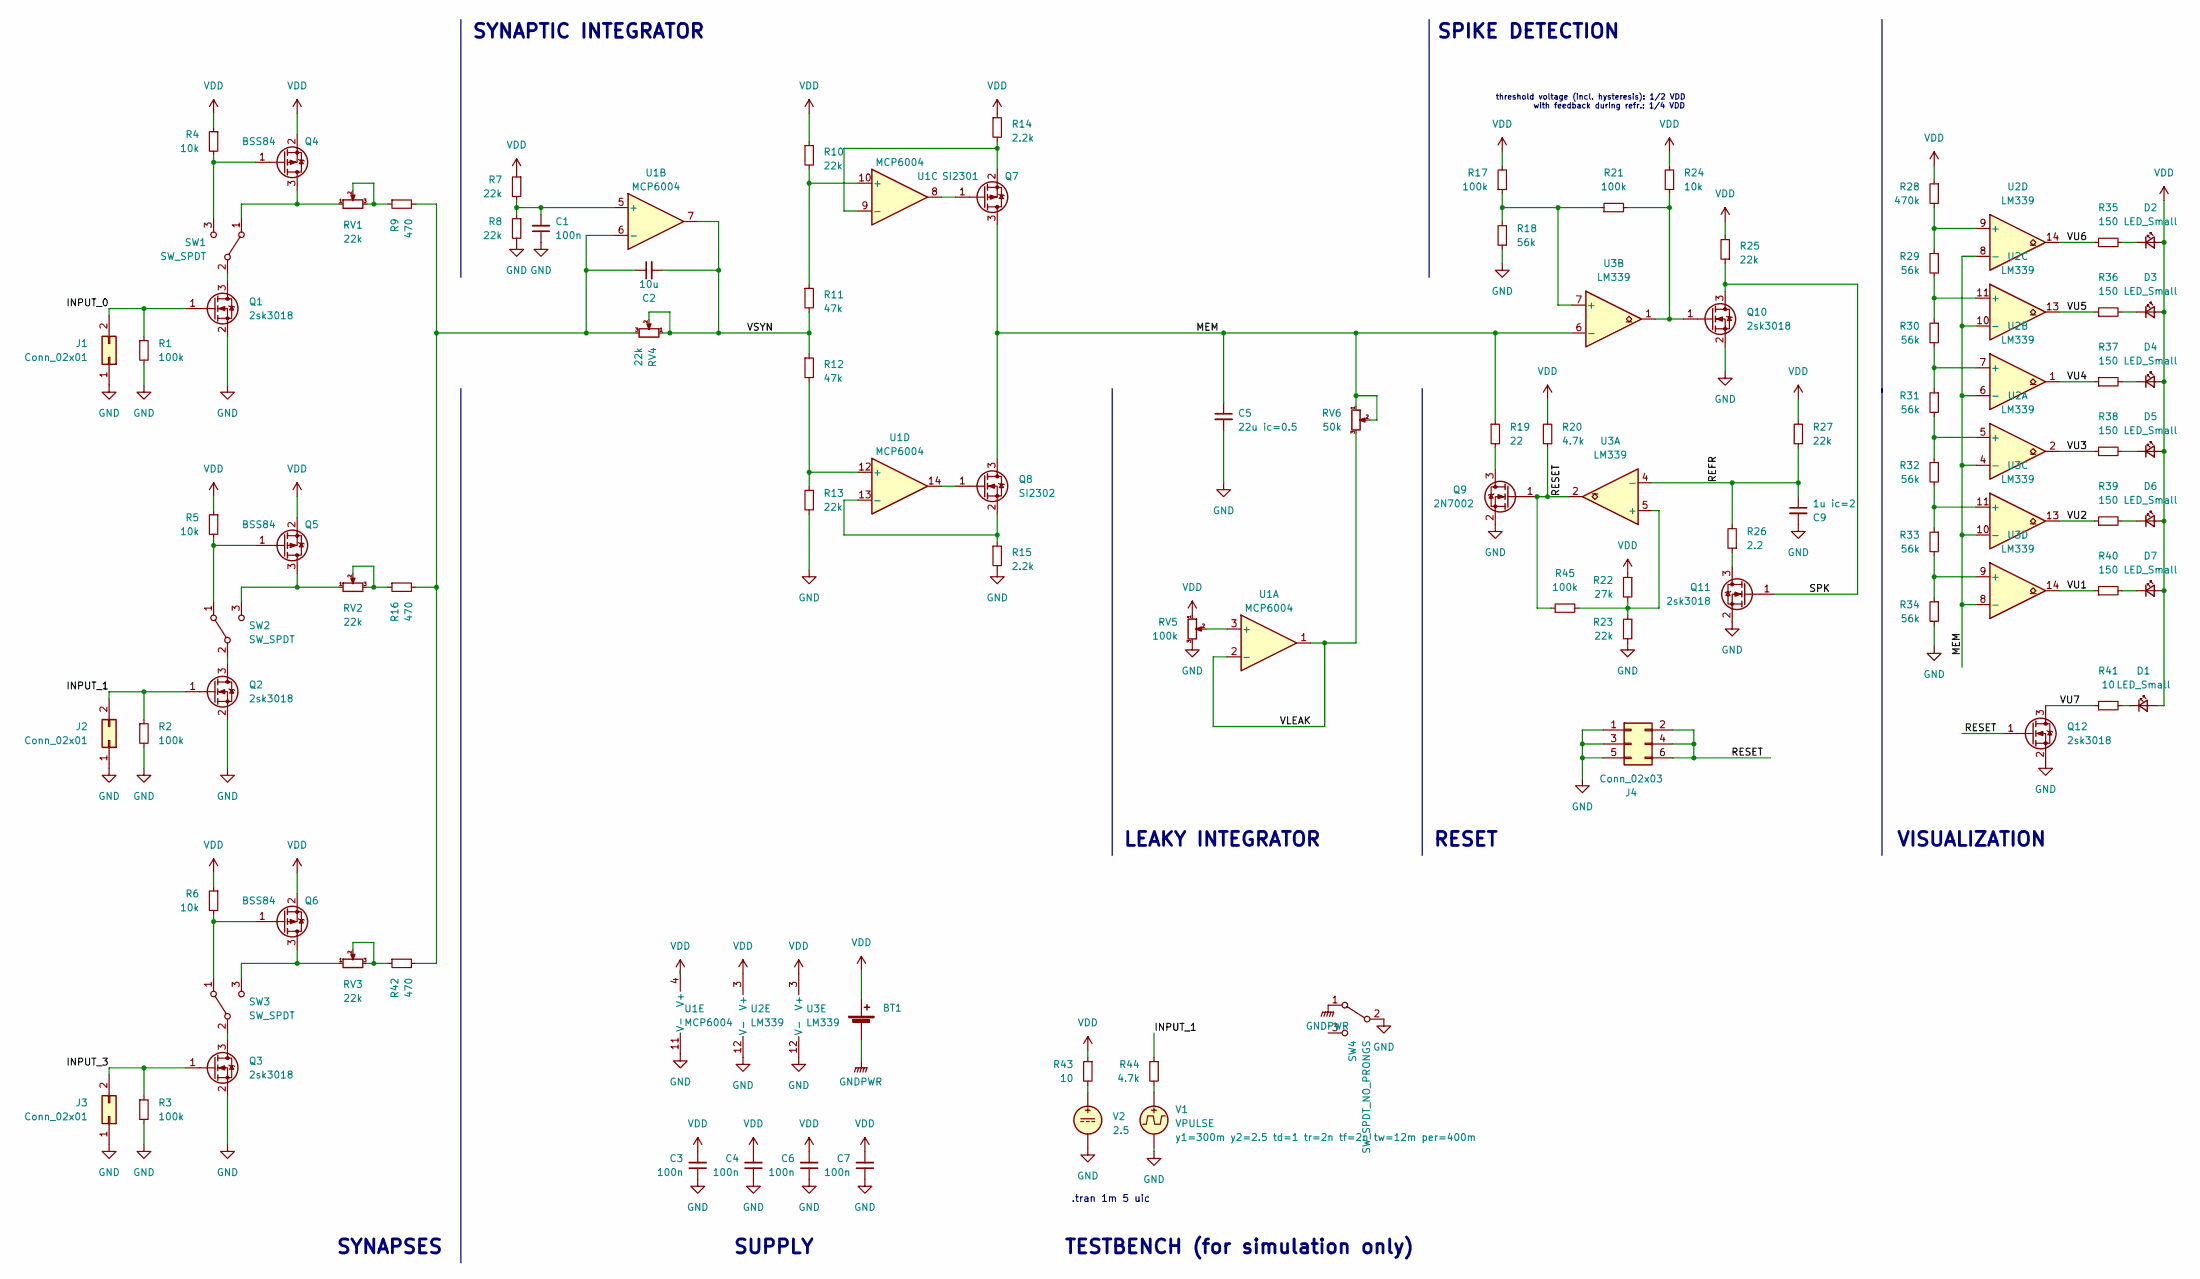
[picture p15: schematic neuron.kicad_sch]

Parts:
BT1: type="R" model="Battery_Cell" lib=""; CR2032_Holder; LCSC C70377
C1, C3, C4, C6, C7: 100n; C_0402_1005Metric; LCSC C1525
C2: 10u; C_0402_1005Metric; LCSC C15525
C5: 22u ic=0.5; C_0402_1005Metric; LCSC C415703
C9: 1u ic=2; C_0402_1005Metric; LCSC C52923
D1, D2, D3, D4, D5, D6, D7: LED_Small; LED_0402_1005Metric; LCSC C779450
J1, J2, J3: Conn_02x01; PinHeader_1x02_P2.54mm_Vertical; LCSC C2894925
J4: Conn_02x03; PinHeader_2x03_P2.54mm_Vertical; LCSC C492420
Q1, Q2, Q3, Q10, Q11, Q12: 2sk3018; SOT-23; LCSC C181084
Q4, Q5, Q6: BSS84; SOT-23; LCSC C8492
Q7: SI2301; SOT-23; LCSC C10487
Q8: SI2302; SOT-23; LCSC C10488
Q9: 2N7002; SOT-23; LCSC C8545
R1, R2, R3, R17, R21, R45: 100k; R_0402_1005Metric; LCSC C25741
R4, R5, R6, R24: 10k; R_0402_1005Metric; LCSC C25744
R7, R8, R10, R13: 22k; R_0402_1005Metric; LCSC C326601
R9, R16, R42: 470; R_0402_1005Metric; LCSC C25117
R11, R12: 47k; R_0402_1005Metric; LCSC C5152005
R14, R15: 2.2k; R_0402_1005Metric; LCSC C705646
R18, R29, R30, R31, R32, R33, R34: 56k; R_0402_1005Metric; LCSC C25796
R19: 22; R_0402_1005Metric; LCSC C25092
R20: 4.7k; R_0402_1005Metric; LCSC C25900
R22: 27k; R_0402_1005Metric; LCSC C25771
R23, R25, R27: 22k; R_0402_1005Metric; LCSC C25768
R26: 2.2; R_0402_1005Metric; LCSC C25101
R28: 470k; R_0402_1005Metric; LCSC C25790
R35, R36, R37, R38, R39, R40: 150; R_0402_1005Metric; LCSC C25082
R41: 10; R_0402_1005Metric; LCSC C25077
R43: 10; R_0402_1005Metric; LCSC C25768
R44: 4.7k; R_0402_1005Metric; LCSC C25768
RV1, RV2, RV3, RV4: 22k; Potentiometer; LCSC C128552
RV5: 100k; Potentiometer; LCSC C128545
RV6: 50k; Potentiometer; LCSC C145161
SW1, SW2, SW3: SW_SPDT; K3-1296S-E1; LCSC C128955
SW4: SW_SPDT_NO_PRONGS; SSAJ120100; LCSC C160864
U1: MCP6004; TSSOP-14_4.4x5mm_P0.65mm; LCSC C50282
U2, U3: LM339; TSSOP-14_4.4x5mm_P0.65mm; LCSC C42184
V1: VPULSE
V2: 2.5

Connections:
/INPUT_0: J1.2, Q1.1 (G), R1.1
/INPUT_1: J2.2, Q2.1 (G), R2.1, R44.1
/INPUT_3: J3.2, Q3.1 (G), R3.1
/MEM: C5.1, Q7.3 (D), Q8.3 (D), R19.1, RV6.1, RV6.2, U2.4 (-), U2.6 (-), U2.8 (-), U2.10 (-), U3.6 (-), U3.8 (-), U3.10 (-)
/REFR: C9.1, R26.2, R27.1, U3.4 (-)
/RESET: J4.2, J4.4, J4.6, Q9.1 (G), Q12.1 (G), R20.1, R45.1, U3.2
/SPK: Q10.3 (D), Q11.1 (G), R25.1
/VLEAK: RV6.3, U1.1, U1.2 (-)
/VSYN: C2.2, R11.2, R12.1, RV4.1, RV4.2, U1.7
/VU1: R40.1, U3.14
/VU2: R39.1, U3.13
/VU3: R38.1, U2.2
/VU4: R37.1, U2.1
/VU5: R36.1, U2.13
/VU6: R35.1, U2.14
/VU7: Q12.3 (D), R41.1
GND: C1.1, C3.1, C4.1, C5.2, C6.1, C7.1, C9.2, J1.1, J2.1, J3.1, J4.1, J4.3, J4.5, Q1.2 (S), Q2.2 (S), Q3.2 (S), Q9.2 (S), Q10.2 (S), Q11.2 (S), Q12.2 (S), R1.2, R2.2, R3.2, R8.2, R13.2, R15.2, R18.1, R23.2, R34.2, RV5.3, SW4.2 (B), U1.11 (V-), U2.12 (V-), U3.12 (V-), V1.2, V2.2
GNDPWR: BT1.2 (-), SW4.1 (A)
unnamed: D1.1 (K), R41.2
unnamed: D2.1 (K), R35.2
unnamed: D3.1 (K), R36.2
unnamed: D4.1 (K), R37.2
unnamed: D5.1 (K), R38.2
unnamed: D6.1 (K), R39.2
unnamed: D7.1 (K), R40.2
unnamed: Q1.3 (D), SW1.2 (B)
unnamed: Q2.3 (D), SW2.2 (B)
unnamed: Q3.3 (D), SW3.2 (B)
unnamed: Q4.3 (D), RV1.1, SW1.1 (A)
unnamed: Q4.1 (G), R4.2, SW1.3 (C)
unnamed: Q5.3 (D), RV2.1, SW2.3 (C)
unnamed: Q5.1 (G), R5.2, SW2.1 (A)
unnamed: Q6.3 (D), RV3.1, SW3.3 (C)
unnamed: Q6.1 (G), R6.2, SW3.1 (A)
unnamed: Q7.1 (G), U1.8
unnamed: Q7.2 (S), R14.2, U1.9 (-)
unnamed: Q8.1 (G), U1.14
unnamed: Q8.2 (S), R15.1, U1.13 (-)
unnamed: Q9.3 (D), R19.2
unnamed: Q10.1 (G), R21.2, R24.1, U3.1
unnamed: Q11.3 (D), R26.1
unnamed: R9.1, RV1.2, RV1.3
unnamed: R16.1, RV2.2, RV2.3
unnamed: R42.1, RV3.2, RV3.3
unnamed: R43.2, V2.1
unnamed: R44.2, V1.1
unnamed: RV5.2, U1.3 (+)
unnamed: C1.2, R7.2, R8.1, U1.5 (+)
unnamed: C2.1, R9.2, R16.2, R42.2, RV4.3, U1.6 (-)
unnamed: R10.2, R11.1, U1.10 (+)
unnamed: R12.2, R13.1, U1.12 (+)
unnamed: R31.2, R32.1, U2.5 (+)
unnamed: R30.2, R31.1, U2.7 (+)
unnamed: R29.2, R30.1, U2.11 (+)
unnamed: R28.2, R29.1, U2.9 (+)
unnamed: R22.2, R23.1, R45.2, U3.5 (+)
unnamed: R17.1, R18.2, R21.1, U3.7 (+)
unnamed: R32.2, R33.1, U3.11 (+)
unnamed: R33.2, R34.1, U3.9 (+)
VDD: BT1.1 (+), C3.2, C4.2, C6.2, C7.2, D1.2 (A), D2.2 (A), D3.2 (A), D4.2 (A), D5.2 (A), D6.2 (A), D7.2 (A), Q4.2 (S), Q5.2 (S), Q6.2 (S), R4.1, R5.1, R6.1, R7.1, R10.1, R14.1, R17.2, R20.2, R22.1, R24.2, R25.2, R27.2, R28.1, R43.1, RV5.1, U1.4 (V+), U2.3 (V+), U3.3 (V+)

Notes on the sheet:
LEAKY INTEGRATOR
RESET
SPIKE DETECTION
TESTBENCH (for simulation only)
SYNAPTIC INTEGRATOR
SYNAPSES
SUPPLY
.tran 1m 5 uic
threshold voltage (incl. hysteresis): 1/2 VDD with feedback during refr.: 1/4 VDD
VISUALIZATION

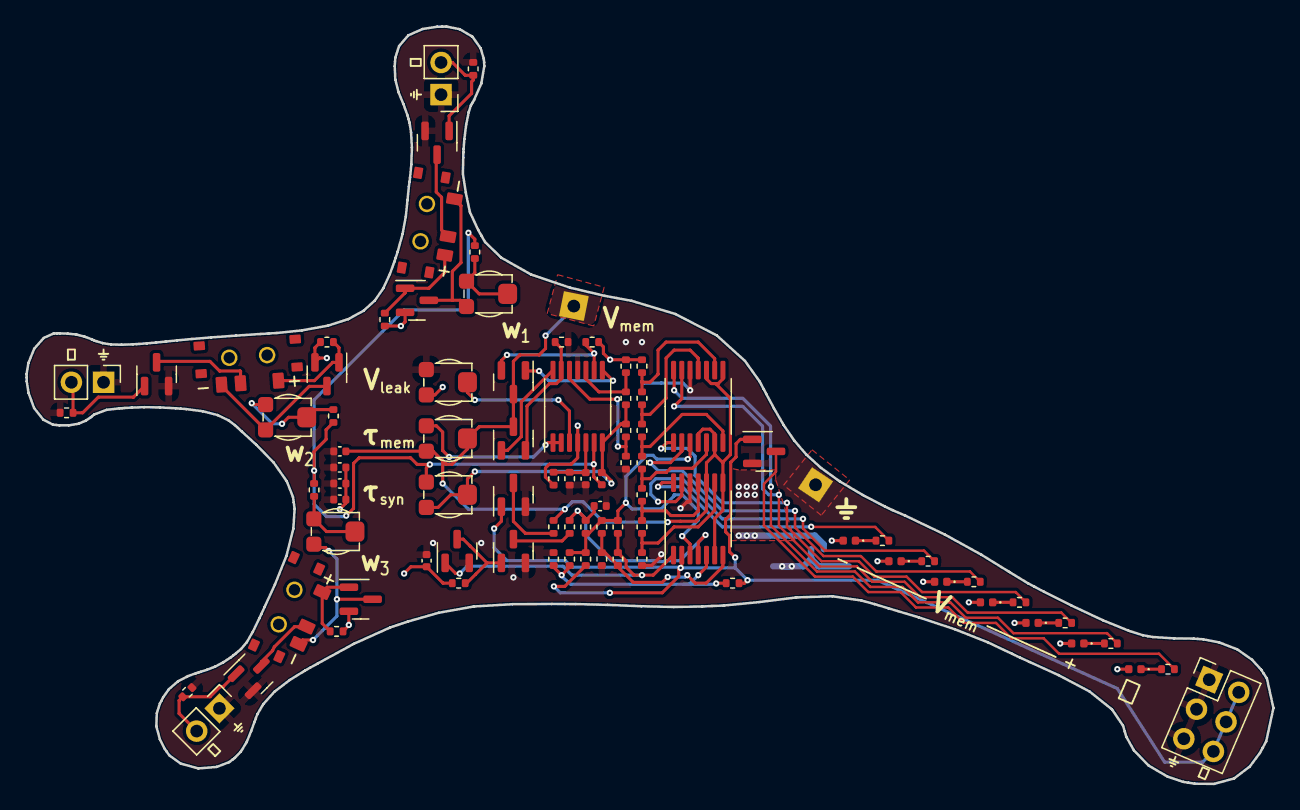
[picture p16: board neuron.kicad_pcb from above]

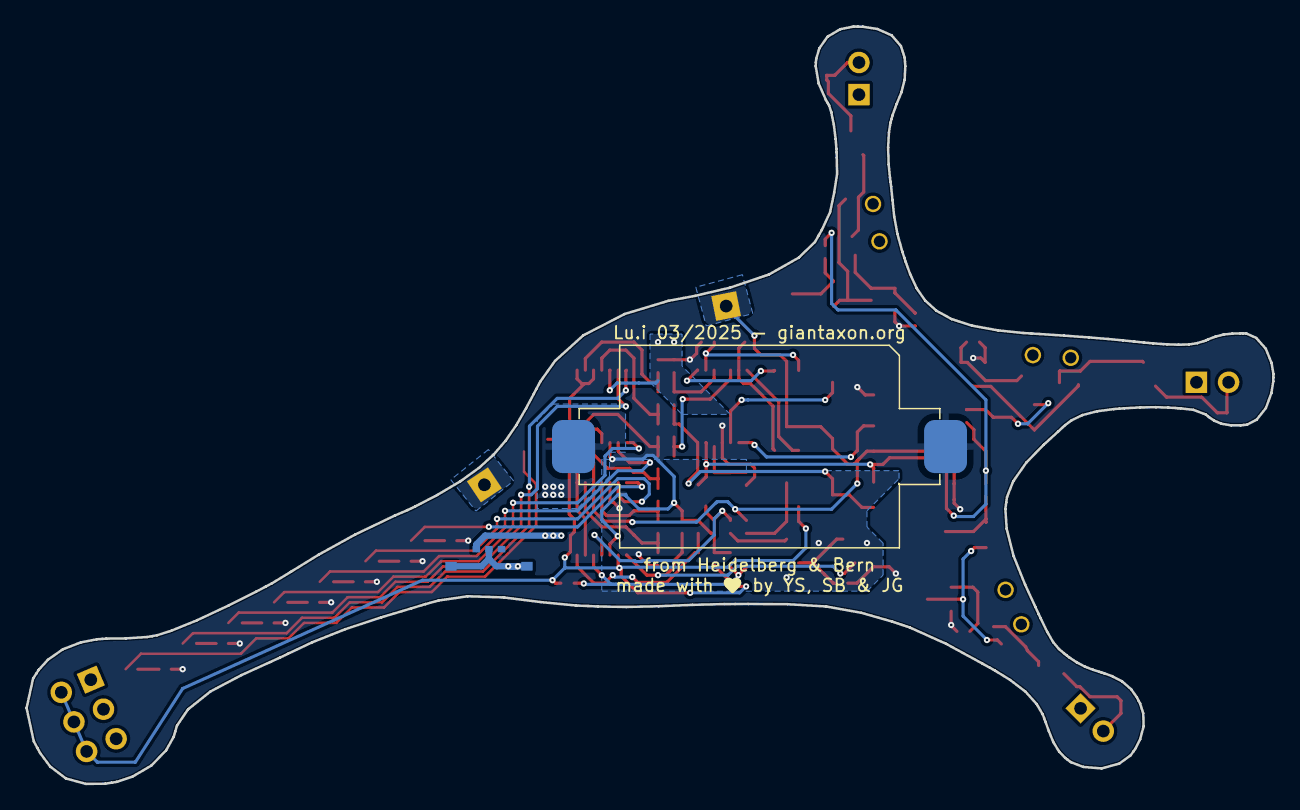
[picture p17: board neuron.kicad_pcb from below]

Board: 2 copper layers, 98.5 x 59.8 mm, 88 parts (2 on the bottom side), 58 nets.

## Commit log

2023-04-05 Migrate to KiCad 7
    [neuron.kicad_pcb, neuron.kicad_sch]
2023-04-05 Update for second production run
    [neuron.kicad_pcb, neuron.kicad_sch]
2023-04-12 Implement exponential synapses
    [neuron.kicad_pcb, neuron.kicad_sch]
2023-04-12 Update comments in schematic
    [neuron.kicad_sch]
2023-04-13 Clean up simulation models and testbench
    [neuron.kicad_pcb, neuron.kicad_sch]
2023-04-13 Clean up schematic
    [neuron.kicad_sch]
2023-04-13 Update 2N7002 simulation model
    [neuron.kicad_sch]
2023-06-07 Replace synaptic time constant and weight potentiometers by 22k
    [neuron.kicad_sch]
2023-06-07 Replace membrane capacitor by more common part
    [neuron.kicad_sch]
2023-06-07 Replace LEDs by more yellow one
    [neuron.kicad_sch]
2023-08-04 Change LEDs due to stock shortages
    [neuron.kicad_sch]
2023-08-04 Annotate board from schematic
    [neuron.kicad_pcb]
2023-11-02 Update README.md
    Add battery type, Spike IO
2024-06-12 Add (optional) power switch on back side
    [neuron.kicad_pcb, neuron.kicad_sch]
2025-03-31 Migrate to KiCAD 9
    [neuron.kicad_pcb, neuron.kicad_sch]
2025-03-31 Re-import schematic to PCB
    [neuron.kicad_pcb]
2025-03-31 Add hysteresis for refractory time comparator
    [neuron.kicad_pcb, neuron.kicad_sch]
2025-03-31 Update layout
    [neuron.kicad_pcb]
